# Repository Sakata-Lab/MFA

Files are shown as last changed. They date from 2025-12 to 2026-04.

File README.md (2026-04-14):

# Multi-fiber array (MFA)-based photometry system
This page provides resources for the publication on MFA development

## system
The folder contains an Excel file with a parts list to construct the optical system.

## grids
The folder contains three .stl files and a Python-based FreeCAD macro.

## fabrication
There is a PDF file detailing MFA fabrication procedures.

## MFA image processing workflow
The MATLAB LiveScript is the workflow for processing a .cxd file to analyse photometry signals.

## mfaCTpy: Python-based package for micro-CT image processing
https://github.com/Sakata-Lab/mfaCTpy 

This package allows:
- file conversion from .dicom files to a .tif file
- alignment to the midline
- registration to the Allen CCFv3
- manual tracing of individual fibers

## citation
If you find our work helpful, please use the following citations.
```
Multi-fiber array-based photometry system for multi-regional functional mapping in the mouse brain
Manil Bradai, Mirna Merkler, Gabriela Gil, Rebecca Davie, Shuzo Sakata
bioRxiv 2025.12.23.696162; doi: https://doi.org/10.64898/2025.12.23.696162

Multi-fiber array-based mesoscopic photometry  in the mouse brain
Manil Bradai, Mirna Merkler, Gabriela Gil, Rebecca Davie, Shuzo Sakata
https://github.com/Sakata-Lab/MFA
```

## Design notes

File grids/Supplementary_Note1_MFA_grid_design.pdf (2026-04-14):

## Supplementary Note 1

# Grid fabrication guide for multi-fiber array photometry system

Sakata Lab

## Introduction

For the multi-fiber array (MFA) photometry system (Bradai et al., bioRxiv 2025), 3D-printed grids are required to construct an MFA. The grid allows arranging multiple optical fibers to target multiple brain regions for various photometry experiments in vivo. In this document, we provide a manual to prepare grids with additional technical notes.

## Workflow

1. Designing a grid in FreeCAD
2. Exporting a CAD file as .stl file
3. 3D printing with Projection Micro Stereolithography (PµSL) technology

## 1. Designing a grind in FreeCAD

- Open FreeCAD

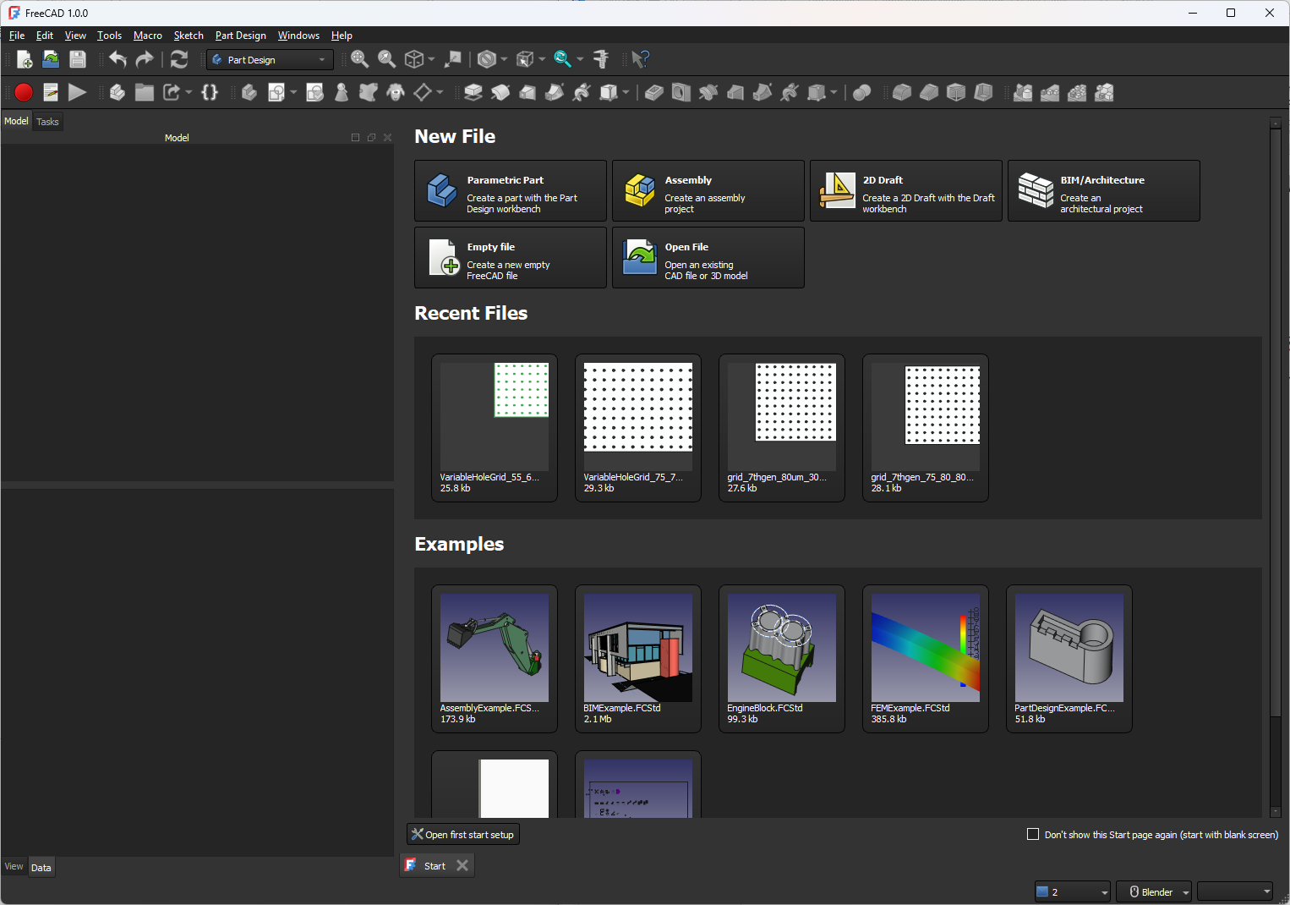
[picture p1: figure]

- File manu “Macro” > “Macros”

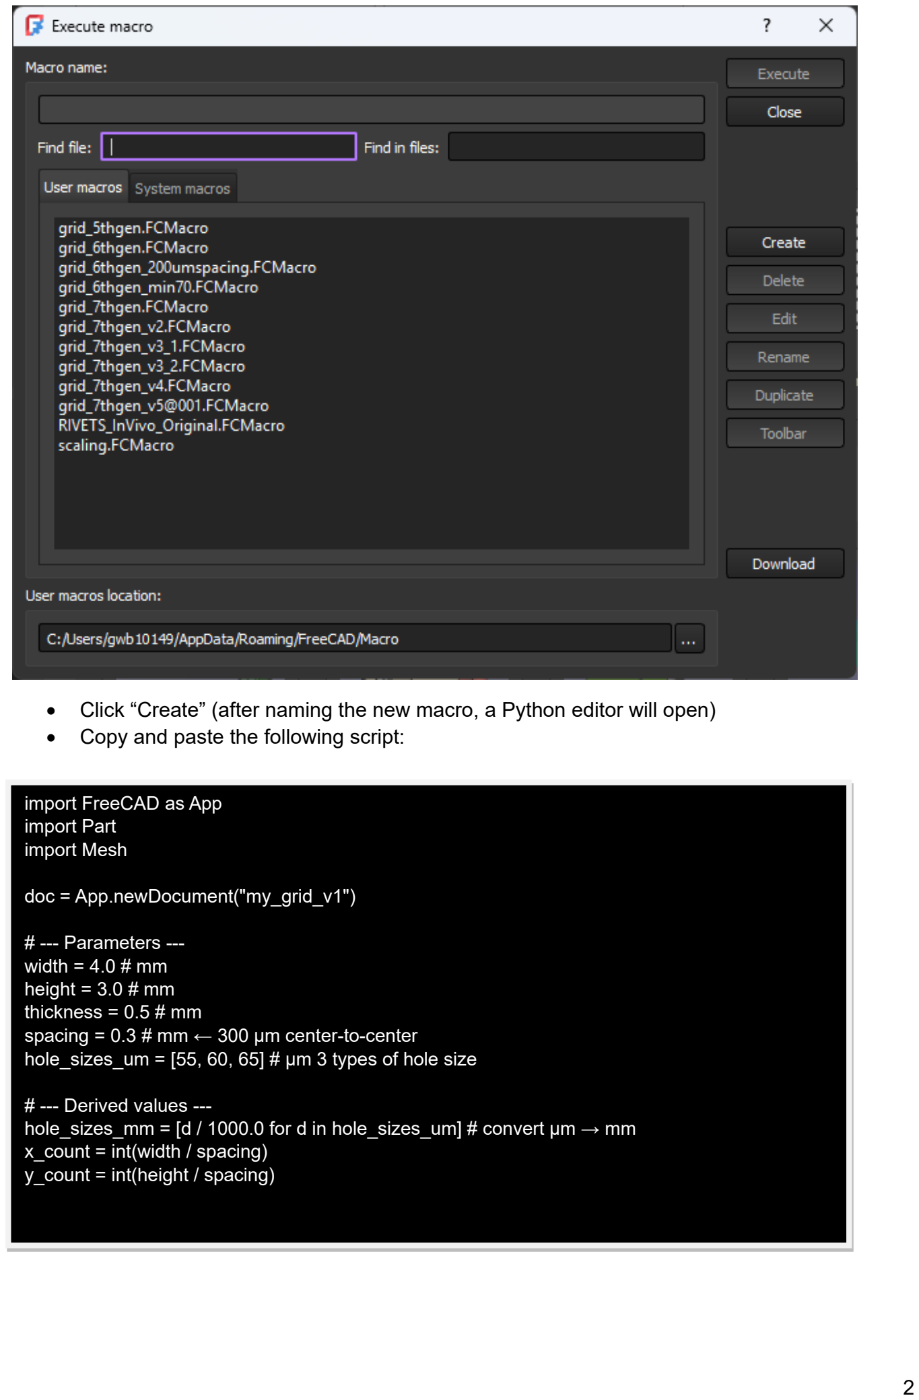
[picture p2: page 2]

- Click “Create” (after naming the new macro, a Python editor will open)
- Copy and paste the following script:

import FreeCAD as App
import Part
import Mesh

doc = App.newDocument("my_grid_v1")

# --- Parameters ---

width = 4.0 # mm
height = 3.0 # mm
thickness = 0.5 # mm
spacing = 0.3 # mm ← 300 µm center-to-center hole_sizes_um = [55, 60, 65] # µm 3 types of hole size

# --- Derived values ---

hole_sizes_mm = [d / 1000.0 for d in hole_sizes_um] # convert µm → mm x_count = int(width / spacing)
y_count = int(height / spacing)

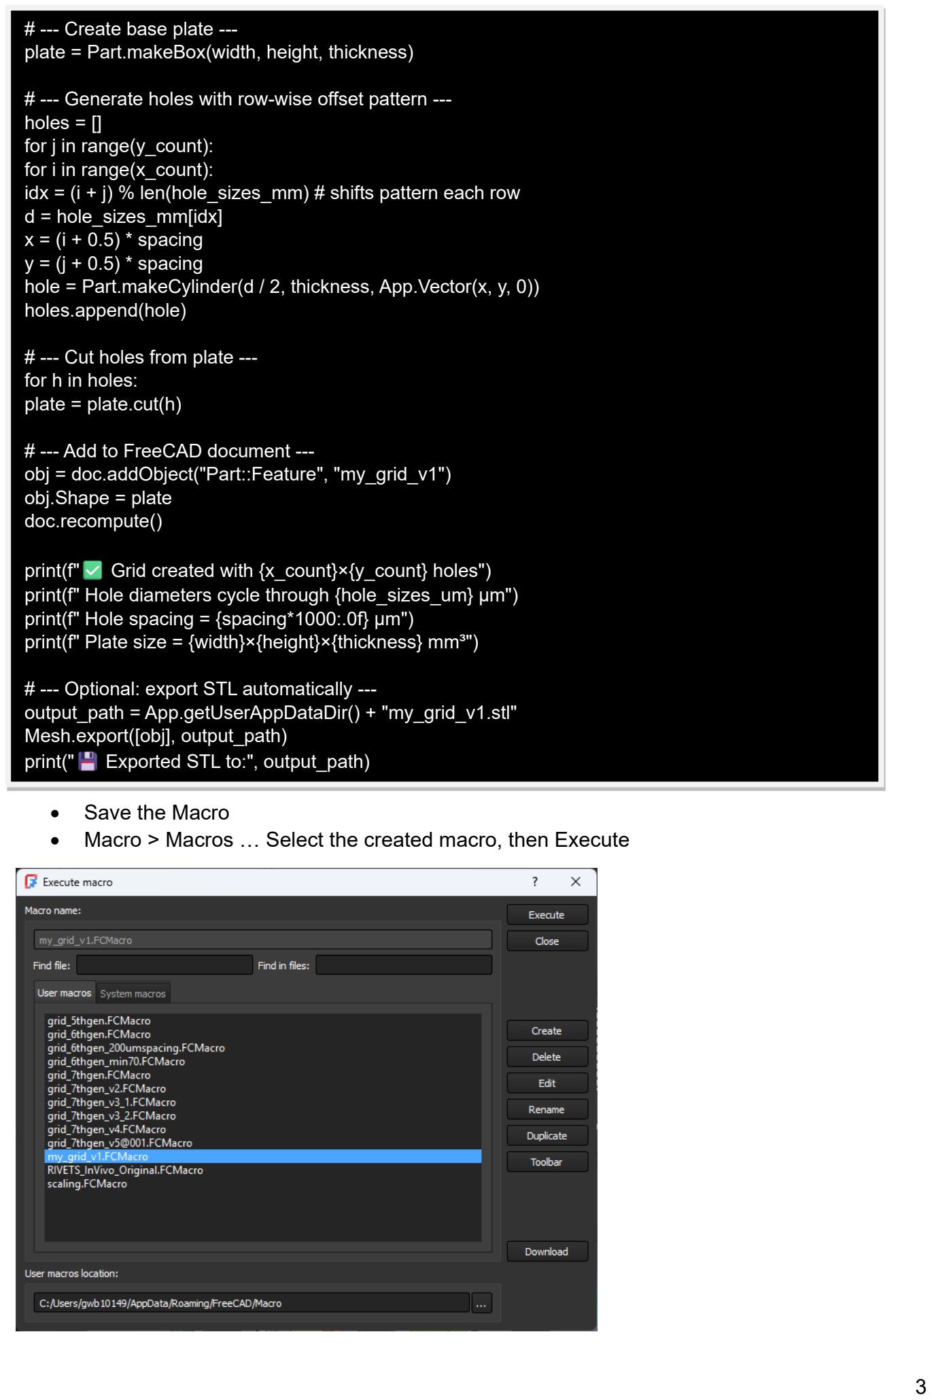
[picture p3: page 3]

- Save the Macro
- Macro > Macros … Select the created macro, then Execute

# --- Create base plate ---

plate = Part.makeBox(width, height, thickness)

# --- Generate holes with row-wise offset pattern ---holes = []

for j in range(y_count):
for i in range(x_count):
idx = (i + j) % len(hole_sizes_mm) # shifts pattern each row d = hole_sizes_mm[idx]
x = (i + 0.5) * spacing
y = (j + 0.5) * spacing
hole = Part.makeCylinder(d / 2, thickness, App.Vector(x, y, 0)) holes.append(hole)

# --- Cut holes from plate ---

for h in holes:
plate = plate.cut(h)

# --- Add to FreeCAD document ---

obj = doc.addObject("Part::Feature", "my_grid_v1") obj.Shape = plate
doc.recompute()

print(f" Grid created with {x_count}×{y_count} holes") print(f" Hole diameters cycle through {hole_sizes_um} µm") print(f" Hole spacing = {spacing*1000:.0f} µm")
print(f" Plate size = {width}×{height}×{thickness} mm³")

# --- Optional: export STL automatically ---

output_path = App.getUserAppDataDir() + "my_grid_v1.stl" Mesh.export([obj], output_path)
print(" Exported STL to:", output_path)

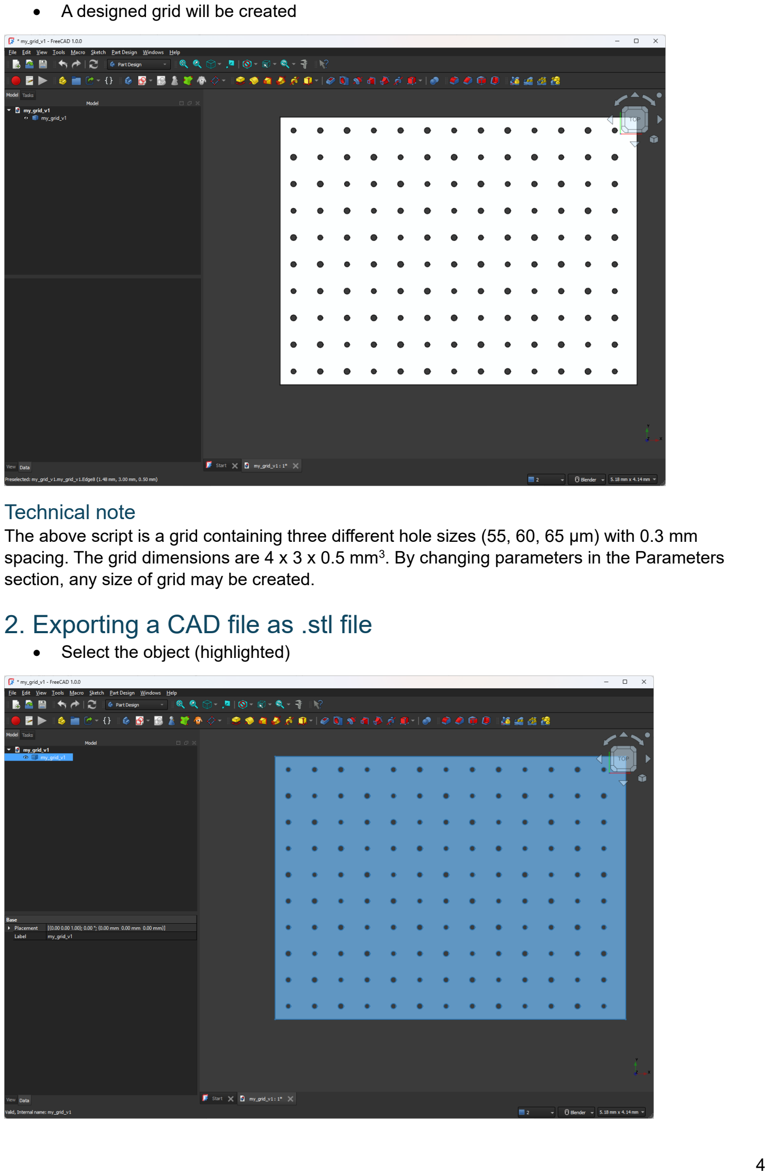
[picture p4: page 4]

- A designed grid will be created

Technical note
The above script is a grid containing three different hole sizes (55, 60, 65 µm) with 0.3 mm spacing. The grid dimensions are 4 x 3 x 0.5 mm³
. By changing parameters in the Parameters section, any size of grid may be created.

## 2. Exporting a CAD file as .stl file

- Select the object (highlighted)

- File > Export …
- Export as .stl file

## 3. 3D printing with PµSL technology

- Contact the company capable of Project Micro Stereolithography (PµSL) technology
- Sending the exported .stl file, grids can be printed

Company information
- BMF https://bmf3d.com/
- IPFL, https://www.ipfl.co.uk/

Any companies using PµSL, provided by Boston Micro Fabrication (BMF), should be able to print grids.

Technical note
At least two factors may be consulted with a company: (1) materials and (2) resolution
- Materials: High temperature liquid (HTL) is standard, but transparent. For opacity, carbon-based materials may be considered.
- Resolution: 2 µm or 10 µm resolution printing is available. The cost difference may be approximately 3x.

When grids are printed with carbon-based materials with 2 µm resolution, a 65~70 µm hole in the CAD file may be recommended since the actual hole size will become ~60 µm, which is suitable for 50 µm optic fibers.

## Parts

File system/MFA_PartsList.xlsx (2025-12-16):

product name | product number | qty | supplier
CMOS Camera
ORCA-Fusion BT | C15440-20UP | 1 | Hamamatsu Photonics
Main Body
Camera Port | WFA4100 | 1 | Thorlabs
Illumination Cube Housing | WFA2002 | 1
Microscopy Cube Assemly | MDFM-MF2 | 1
Dichroic Filter | MD498 | 1
Emission Filter | MF525-39 | 1
Cerna Body with Epi Arm | CEA1400 | 1
Aluminium Breadboard | MB4560/M | 1
Objective, Arm, Motorized Module
10x Fluorite Objective | RMS10X-PF | 1 | Olympus
Objective Arm | CSN100 | 1 | Thorlabs
Adaptor | M32RMSS | 1
Angle Bracket | PLSZ1 | 1
Motorized Module | PLSZ | 1
Stepper Controller | MCM301 | 1
USB Joystick | MCMK3 | 1
Light Sources
405 nm LED | M405L | 1 | Thorlabs
470 nm LED | M470L | 1
LED Holder | CP12 | 2
LED Driver | LEDD1B | 2
Aspheric Condenser Lens | ACL2520U-A | 2
Lens Tube | SM1L05 | 2
Cage Plate | CP08/M | 2
Filter Holder | C4W | 1
Kinematic Cage Cube Platform | B4C/M | 1
Dichroic Mirror | DMLP425R | 1
Peripheral (face camera)
Camera | aca1920-25um | 1 | Basler
Zoom Lens | M0814-MP2 | 1 | Computar
IR Filter | FGL780 | 1 | Thorlabs
IR LED Array | USB100W05MT-DL36 | 1 | ELP
Peripheral (DAQ)
DAQ Module | NI-USB-6002 | 1 | National Instruments
OR Gate | custom-made | 1 | RS components
Computer | Precision 5860 Tower | 1 | Dell

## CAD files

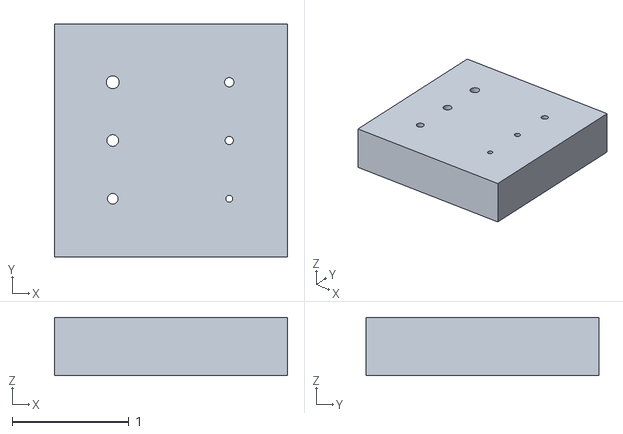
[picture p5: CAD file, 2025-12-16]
grids/grid_various_hole_sizes.stl
2.00 x 2.00 x 0.5

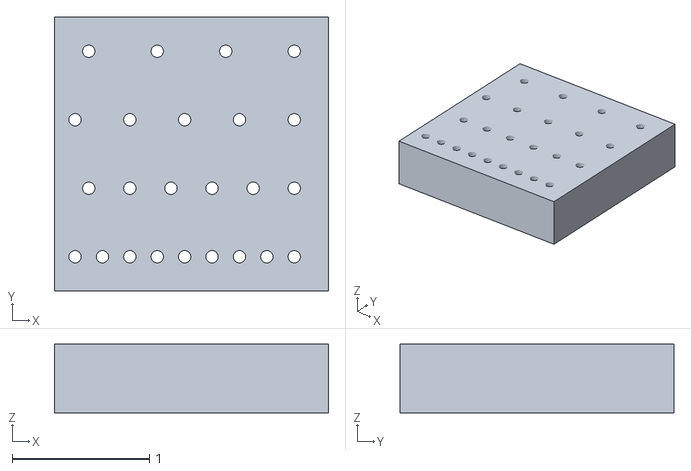
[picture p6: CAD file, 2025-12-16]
grids/grid_various_hole_distance.stl
2.00 x 2.00 x 0.5

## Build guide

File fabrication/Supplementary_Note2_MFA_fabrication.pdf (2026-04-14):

## Supplementary Note 2

# Multi-Fiber Array Construction Manual

## Gabriela Gil and Rebecca Davie

Table of Contents

## 1. Materials and Equipment

## 1.1 Consumables

Item | Manufacturer | Product Information
Optic fibers | Fiberoptics Technology Inc | Purewave XL66 1mmx30 Raw Fibre Bundle, 50µm, NA66
MFA grid | IPFL | Custom design
UV glue | Norland Products, Inc | Norland Optical Adhesive, NOA61, 1 OZ, 28.5g, LOT 612
Black Glue | RS Components | RS Pro, RT80 Black Cyanoacrylate, 20g, RS 908-2802
Pink Zap Glue | ZAP-A-GAP | ZAP CA Thin CA, 1 OZ (28.3g), PT-08
Solder Wire | MBO (UK) Ltd. | Solder Wire, 500g, 547-287
Acrylic Resin Liquid | Kemdent | Simplex Rapid Acrylic Liquid, 150ml, LOT 47557
Polishing Paper (green) | Thorlabs | 6x6 Inch, Diamond Lapping (Polishing) Sheets, 30µm Grit, LF30D
Polishing Paper (yellow) | Thorlabs | 6x6 Inch, Diamond Lapping (Polishing) Sheets, 6µm Grit, LF6D
Polishing Paper (pink) | Thorlabs | 6x6 Inch, Diamond Lapping (Polishing) Sheets, 3µm Grit, LF3D
Tubing | MicroLumen | Polyimide medical tubing, ID: 0.0710, OD:0.0988, Wall: 0.01390, 710-XV.5
Tubing | MicroLumen | Polyimide medical tubing, ID: 0.0477, OD:0.0578, Wall: 0.00505, 475-V.25
Reusable adhesive | Bostik | Blu Tack
Fluorescein HITC | Thermo Scientific Chemicals | Fluorescein Pure, 119240250

## 1.2 Tools and Instruments

Item | Manufacturer | Product Information
Optic fiber scribe | Thorlabs | FiberScribe, S90R
Stereoscope | Olympus | SZ51
Fiber Polishing Pad | Thorlabs | Silicone Polishing Pad, 50 duometer, 8.75x13 Inch (222.3mmx320.2mm) and 0.12Inch Thick (3.1m), NRS913A
Glass Polishing Plate | Thorlabs | Glass Polishing Plate, 9.5x13.5Inch and 0.5Inch Height, CTG913
LED Pen | Cakkone | CAT 2025 2 8
Digital Microscope | Ninyoon | 4K WIFI Microscope, 748521049947
Digital Microscope | Andonstar Technology Co.,Ltd. | AD106S
Tweezers | World Precision Instruments | Dumont Tweezers 5/45
Tweezers | TOWOT | Precision Tweezers, 5pcs Machine Tweezers Made of Stainless Steel Heat Resistant, SA13
Tweezers | Fine Science Tools | Graefe Iris Forceps, 11064-07
Scissors | World Precision Instruments | Operating Scissors 12/21, 501754-G
Optical system | See main text

## 2. Designing a Multi-Fiber Array (MFA)

This section outlines how to plan and design a customized MFA by identifying target brain regions, determining their anatomical coordinates using brain atlases, and arranging fibers on a spatial grid.

- Identify the target brain regions for optical recordings.
- Use the Paxinos and Franklin Mouse Brain Atlas to obtain stereotaxic coordinates for each region of interest.
- Define the MFA grid layout (e.g., 4 × 3 mm).
- Grid dimensions are fully customizable and should be adapted to the spatial distribution of the target regions.
- The spacing used here was 0.3 mm, resulting in linear offsets of 0.3 mm, 0.6 mm, 0.9 mm, etc.
- Note that spacing can be modified depending on experimental requirements.
- Map each fiber position on the grid to its corresponding anatomical target based on the stereotaxic coordinates.
- Adjust fiber lengths to ensure smooth implantation (e.g., adding an extra length to every fiber to improve visibility during implantation).

## 3. Preparation of Optical Fibers

This section covers how to set up a clean, organized workspace and prepare individual optical fibers for later assembly. It includes cutting, inspecting, and selecting viable fiber segments that will form the implantation array.

## 3.1 Workspace Preparation

- Lay out the Thorlabs silicone polishing pad on the Thorlabs glass polishing plate
- Spray the surface with antiseptic spray and wipe to clear any residue.
- Turn on the Andonstar digital microscope, prepare the Thorlabs fiber scribe, ruler and the Purewave fiber bundle.

## 3.2 Cutting and Organising Viable Fibers

- Pull out a fiber (be cautious of the glass) from the Purewave fiber bundle
- Place the fiber on the silicone polishing pad horizontally,
- With a ruler measure out approximate length of 3cm (anything longer can make the later stages harder) (Fig. 1A).
- Cut 3cm fiber segments by aligning the Thorlabs fiber scribe perpendicular to the fiber and gently slice in a one smooth motion
- Note that any excess pressure or pushing the blade directly into the fiber will result in damage.
- Inspect each of the cut fibers by holding them in tweezers no. 5/45 with a little bit of blu tack for better grip under the Andonstar digital microscope.
- Place suitable ends of the fibers facing one direction (these will be the ones used for implantation) (Fig. 1B)

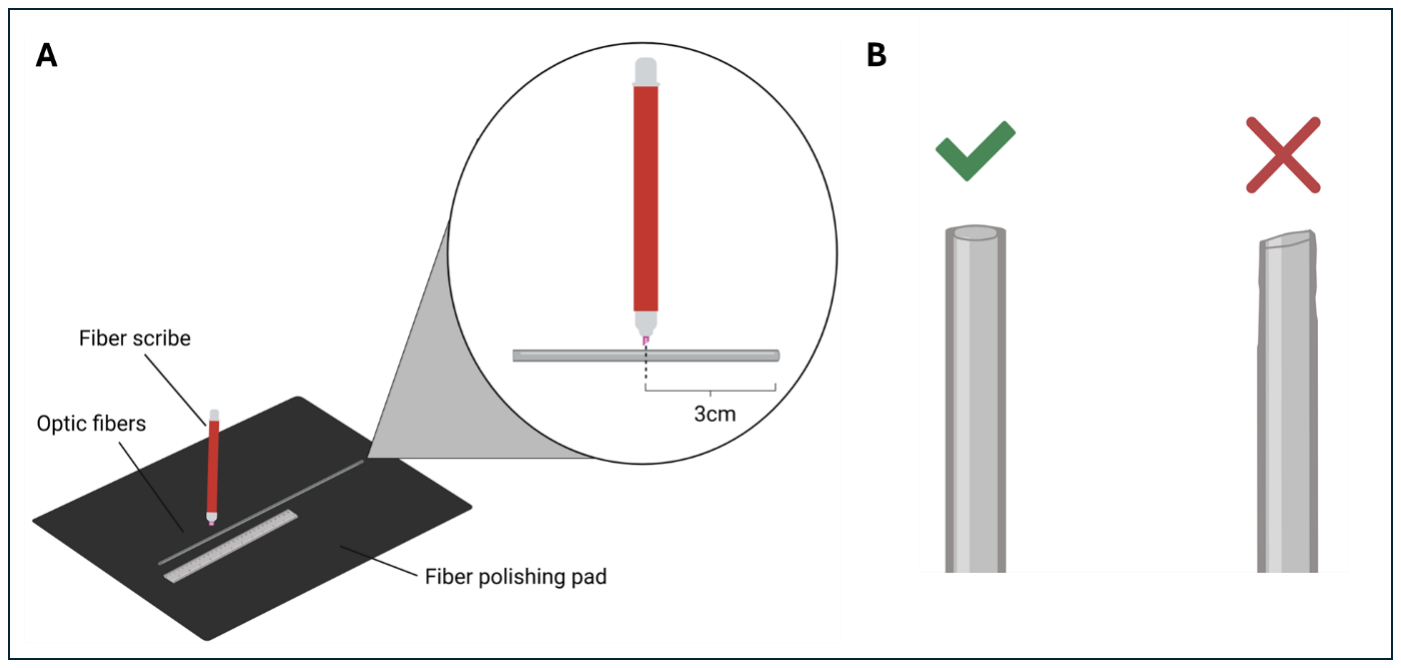
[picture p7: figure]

## 4. Preparing and Mounting the Grid

Explains how to position and stabilise the MFA grid so that its holes are clearly visible and accessible. Proper mounting is essential for successful fiber insertion in the next steps.

- Take the MFA grid (depending on the flexibility of the grid find the best way to mount it) and gently close inside of the tweezer no. SA13 securing vertically in the helping hand (Fig. 2)
- Note: Apply a thin layer of blue tack to inside to better grip
- Adjust the tilt of the grid under the Olympus Stereoscope, the holes of the grid should be all visible
- Check the stability of the set-up, this is crucial for the next step.
Figure 1 | Preparation and Cutting of Optic Fibers. Schematic illustrating the
procedure for cutting optic fibers. (A) A Thorlabs fiber scribe is positioned perpendicular to an optic fiber taken from the Purewave fiber bundle. The scribe is used to cut the fiber, producing a ~3cm segment. (B) Comparison of correct (left) and incorrect (right) fiber preparations following cutting. The left image shows a cleanly cut fiber with a smooth, flat imaging surface suitable for implantation. The right image shows a poorly cut fiber with a damaged, angled imaging surface that is unsuitable for implantation. Figures not to scale. Created in bioRender.

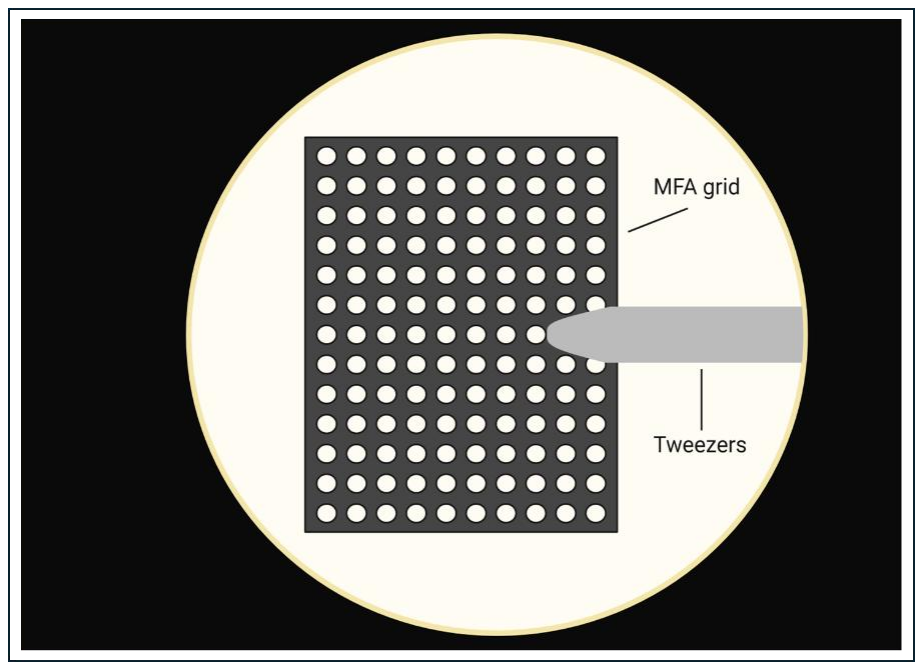
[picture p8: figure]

## 5. Loading Fibers into the Grid

This section describes how to measure implantation depth, mark fibers accordingly, and insert them into the grid in an organised, damage-minimising sequence. It concludes with securing all implanted fibers in place with adhesive.

## 5.1 Measuring Implantation Depth

- Using callipers measure out the length of the fiber implantation depth (Fig. 3)
- Note: refer to the MFA design ensure to factor in the thickness of the grid (0.5 mm) and offset (1 mm) for visualization of the brain surface during implantation.
- Use a soldering wire to place a drop Norland Optical Adhesive to mark the point of measured depth.
- Treat the adhesive drop with UWAVE curing pen for around 20 seconds (take any necessary precautions when using the UV light).
Figure 2 | MFA Grid Setup. Schematic representation of the stereoscopic view of the
MFA grid prior to fiber insertion. The grid is positioned between tweezers (no. SA13) lined with a thin layer of blu tack. The tweezers are held in place using helping hands. Figure not to scale. Created in bioRender.

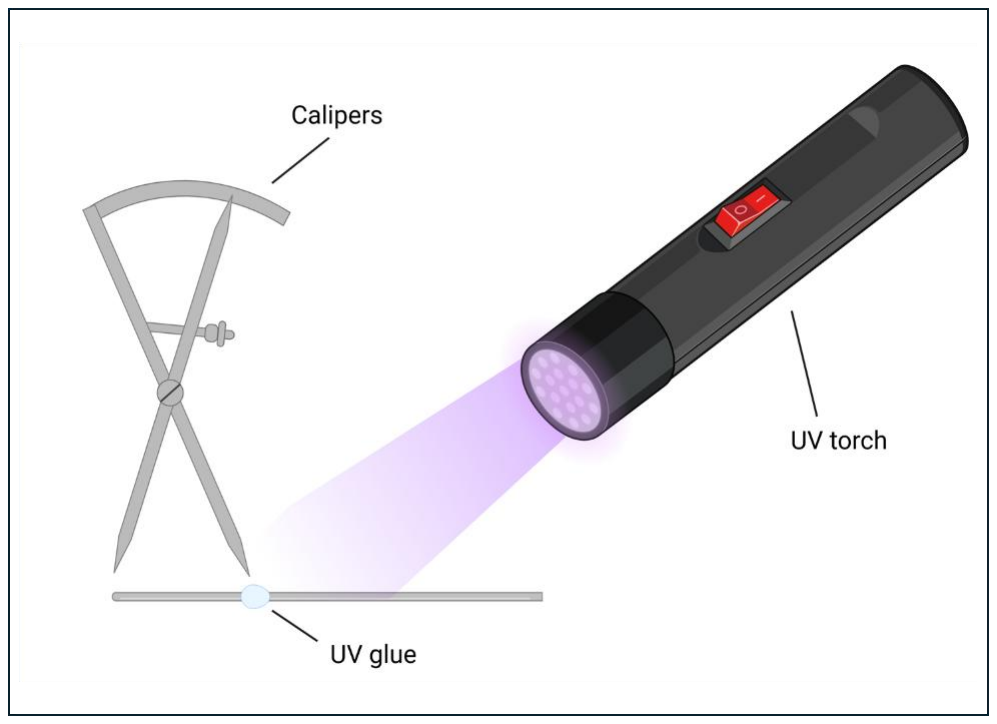
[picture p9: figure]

## 5.2 Insertion Procedure and Securing Fibers in Grid

- In reference to the MFA design, start from the top of the grid and work your way across the rows (this will help avoid the distal ends of the fibers breaking) (Fig. 4A).
- To insert the cured fibers, use blue tack lined tweezers no. 5/45 and hold approximately 1/3 from the implantation end to insert cured fibers into assigned grid hole
- Note: avoid tapping the end on the grid as this may result in the site being fractured = low efficiency.
- Once all the fibers have been inserted (Fig. 4B), carefully tilt the grid so that it lies perfectly parallel to the workbench.
- Using the soldering wire, place drops of UV glue (NOA61, Norland Products) on the top of the grid. The droplet should spread across the grid, then secure the fibers in place with a UV light.
Figure 3 | Measurement and Marking of Fiber Implantation Depth. Schematic
illustrating the procedure for measuring and marking fiber implantation depths prior to insertion into the MFA grid. Calipers are used to measure the length of the fiber segment to be implanted in reference to the MFA design. The thickness of the grid is included in the final caliper measurement. The measured depth point is marked with UV glue and cured using an UV torch. Figure not to scale. Created in bioRender.

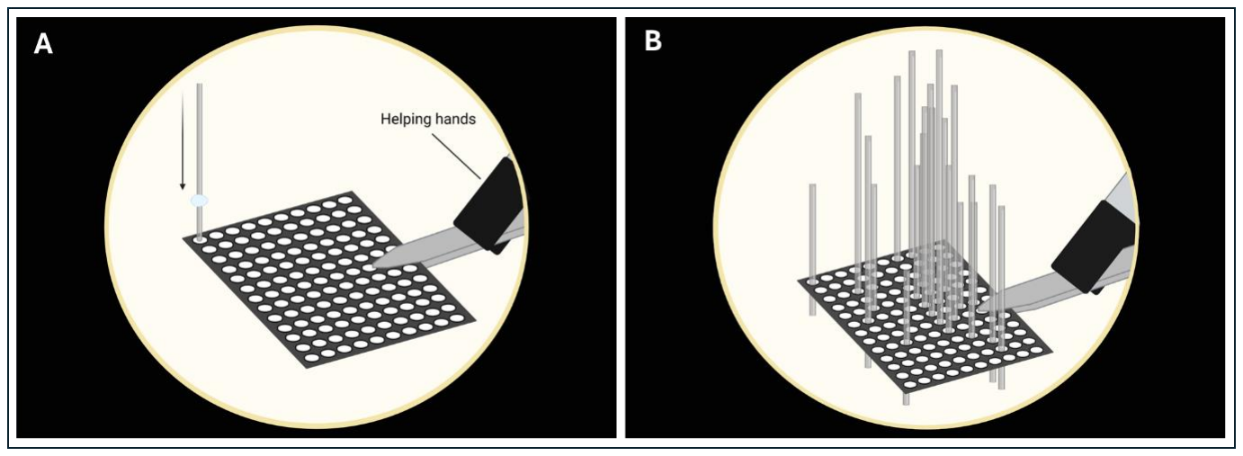
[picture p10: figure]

## 6. Securing and Encasing Distal Fiber Ends

This section describes how to gather, insert, and fix the distal (non-implanting) ends of the fibers inside a protective tube, creating a stable bundle for imaging.

## 6.1 Tubing Placement

- Cut an 8mm piece using a scalpel Microlumen tubing.
- Note: Depending on the number of fibers being implanted choose a suitable size of the Microlumen tubing
- Bundle the distal (non-implanting) ends of the fibers by gently gathering them with moistened fingertips (Fig. 5A)
- Navigate the bundle into the cut Microlumen tubing (Fig. 5B).
Figure 4 | Loading Fibers into the MFA Grid. Schematic representation of the
stereomicroscopic view of the fiber loading process. (A) According to the MFA design, cured fibers are inserted into the MFA grid. Beginning at the top of the grid, fibers are inserted row by row (top to bottom) and column by column (left to right). (B) Shows a fully loaded MFA grid. Figures not to scale. Created in bioRender.

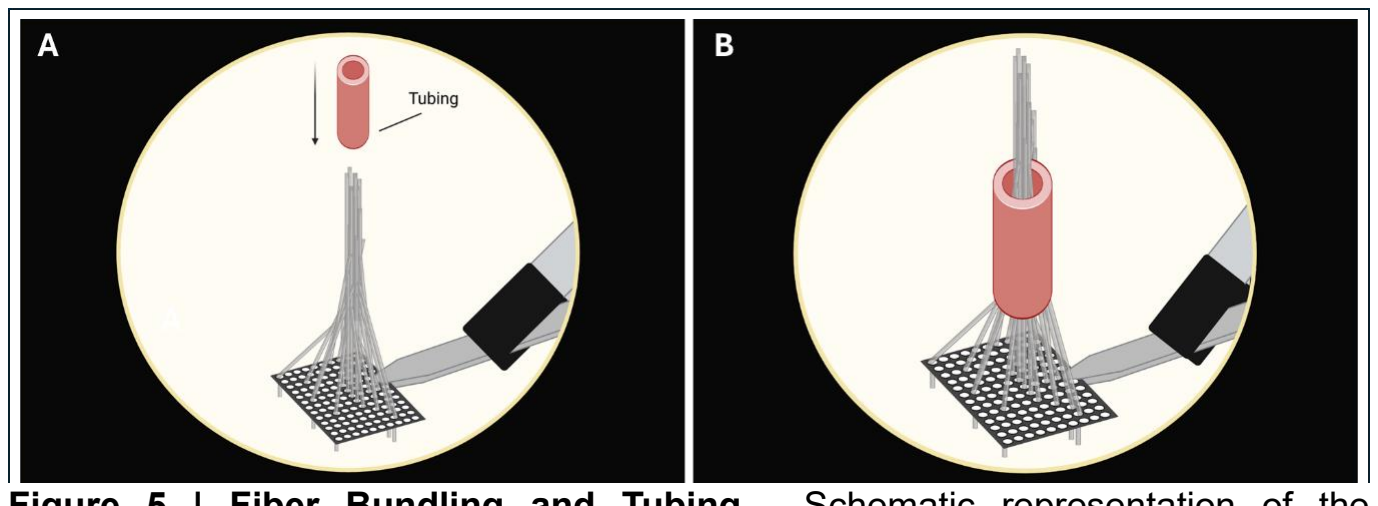
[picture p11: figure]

Figure 5 | Fiber Bundling and Tubing. Schematic representation of the
stereomicroscopic view of fiber bundling and tubing placement process. (A) The distal fiber ends are bundled together using moistened fingertips. (B) Microlumen tubing is then lowered to collect the bundled distal ends. Figures not to scale. Created in bioRender.

## 6.2 Filling Tube with Adhesive

- Using a micro syringe pull ZAP Thin CA glue, avoiding air bubbles (Fig. 6).
- Face the needle towards you, and controlling the decant flow of the glue into the tube fill approximately ¼
- Allow the first layer of glue to dry out (around 10min)
- Once the first layer is dry continue to fill the tube in the same manner, make sure the tube is filled to the brim but not overflowing.
- Leave to dry overnight.
- Note: It is key to avoid air bubbles as this will impact the imaging surface

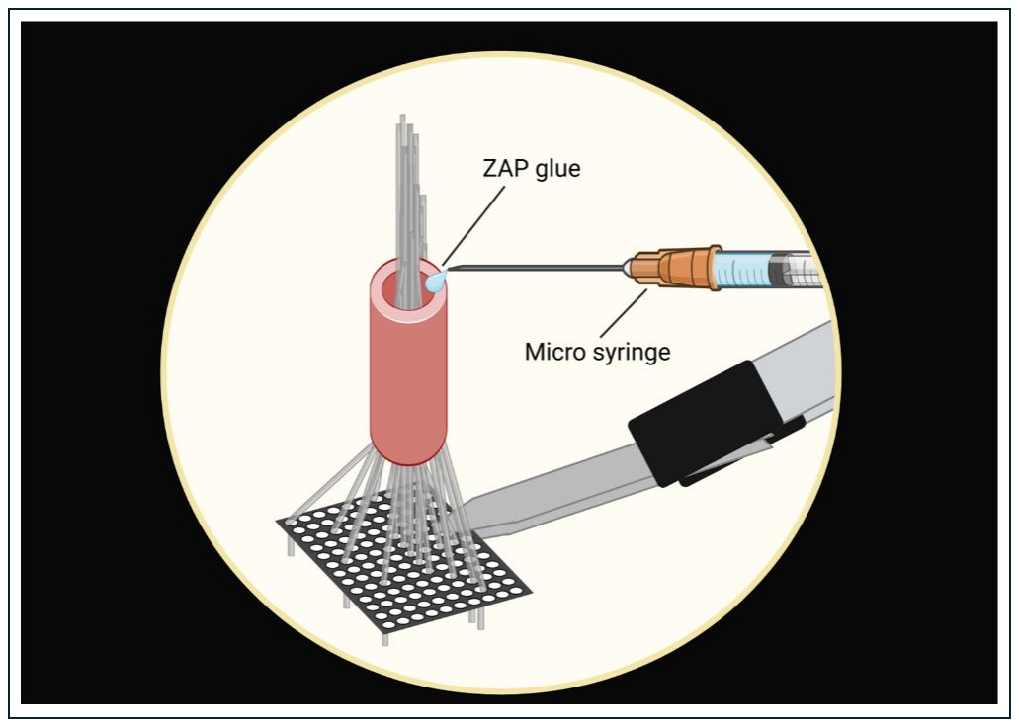
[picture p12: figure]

## 7. Encasing MFA and Polishing the Imaging Surface

This section details how to reinforce the MFA with additional adhesive layers and polish the distal surface to ensure a smooth, optically clean imaging area.

## 7.1 Encasing the grid

- Cut off a short piece of the soldering wire and create a circle
- Slide the Microlumen tube of the MFA halfway into it and tighten the wire, you may wrap the wire around again to ensure stability and twist the ends to secure (Fig. 7A).
Figure 6 | Filling Tubing with Adhesive. Schematic illustrating the process of filling
the microlumen tubing with ZAP glue. A micro syringe is used to draw ZAP glue, which is slowly dispensed into the tubing, allowing approximately 10 minutes between layers. This process is repeated until the tube is filled. Figure not to scale. Created in bioRender.

- Insert the twisted part of the wire into the helping hand and adjust the MFA so that it is parallel to the workbench.
- Use soldering wire to place drops of the RT80 Black Cyanoacrylate to create layers starting from the grid towards the top of the tube. Allow the glue to spread between the fibers (Fig. 7B).
- Allow layers to dry out before proceeding with the next one
- Optional: you can use a drop of Rapid Acrylic liquid to speed the drying process).
- Make sure to cover the red tubing with the black glue to protect the fibers from light and allow to dry

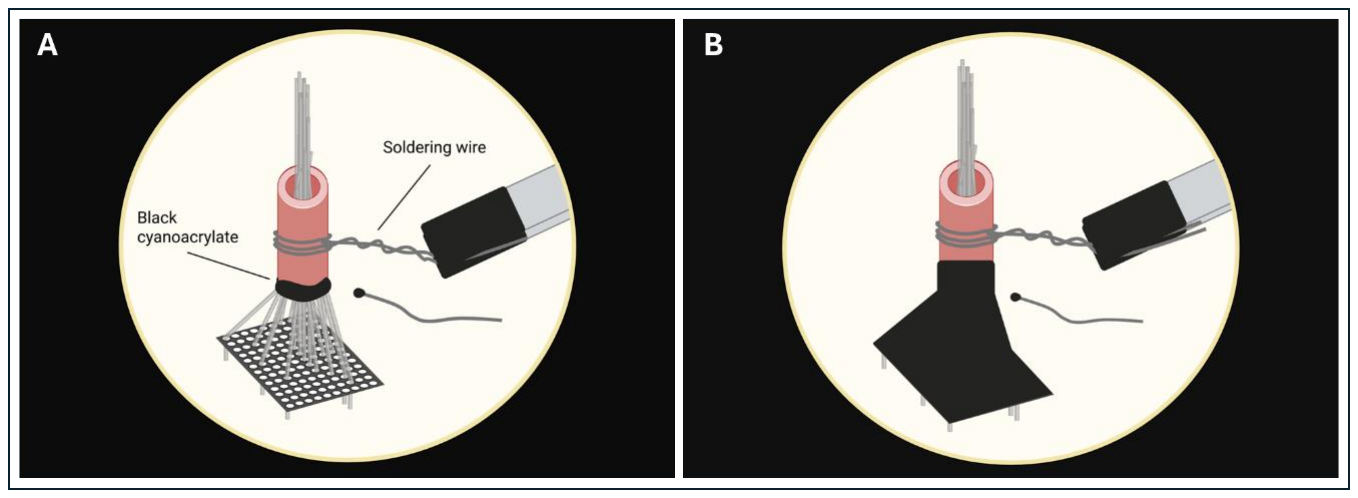
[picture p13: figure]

## 7.2 Rough Cutting and Polishing Sequence

- Use scissors to trim the distal fiber bundle (you may consider cutting part of the tubing along with it) (Fig. 8A).
- Lay out three Thorlabs Diamond Lapping (polishing) sheets of different grit 30µm (green), 6µm (yellow), 3µm (pink).
- Add a drop of distilled water to each of the papers and spread with your finger.
- Grip the tube with tweezers no. 11064-07 and holding the tweezers perpendicular to the paper throughout, using circular motion, polish the surface of the tube for 2 minutes on each of the papers starting with the highest grit (Fig. 8B).
- Using the stereoscope examine the imaging surface, ensure the surface is flat and no major air bubbles are obstructing the imaging area.
- Note: If the surface still looks uneven you may repolish the tube using the 3µm grit.
Figure 7 | Encasing the MFA. Schematic representation of the stereomicroscopic
view of encasing the MFA with black cyanoacrylate. (A) The MFA is repositioned in the helping hands using soldering wire. A segment of soldering wire is dipped in black cyanoacrylate and is used to apply adhesive around the base of the microlumen tubing. (B) A fully encased MFA is shown. Repeat this process, covering the bottom of the microlumen tubing, exposed fibres, and grid is repeated until the MFA is fully encased. Figures not to scale. Created in bioRender.

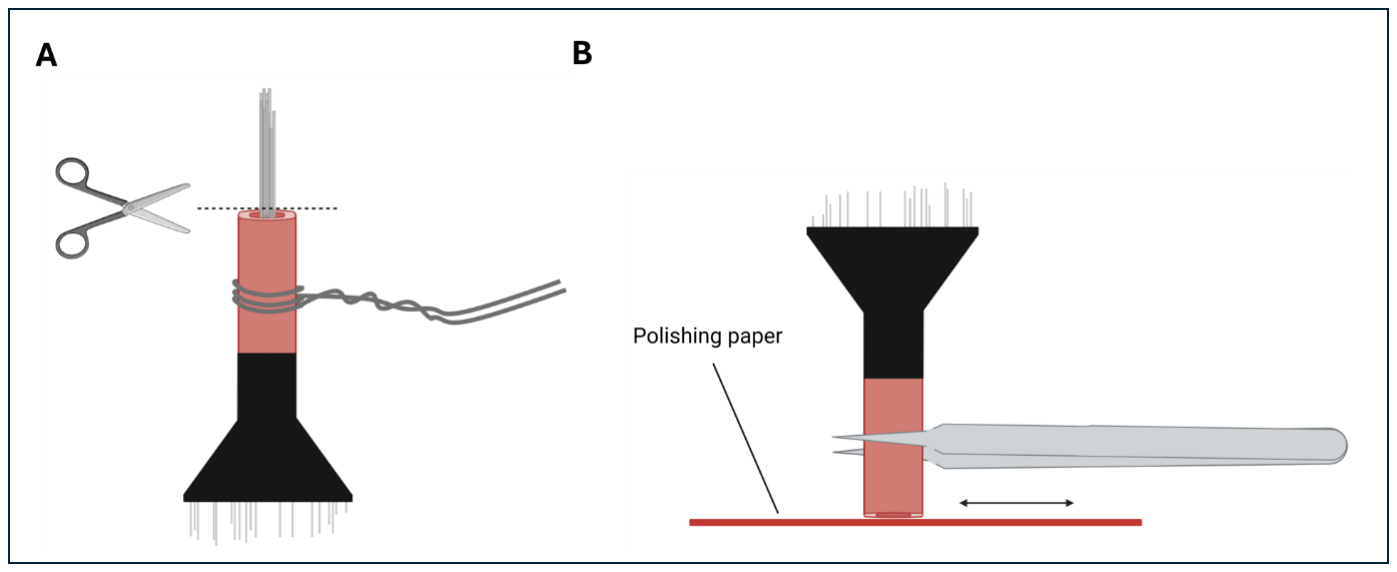
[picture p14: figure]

## 8. Fiber Mapping

This section describes how to identify the correspondence between each implanted fiber’s grid position and its position on the polished imaging surface. This map is essential for later data interpretation.

## 8.1 Setup

- Rotate the MFA so that the implantation site is facing upwards and secure in the helping hands by clamping the twisted soldering wire (Fig. 9).
- Position the Olympus stereoscope so that you can clearly see the implantation fibers and which row/columns they sit in.
- Turn on the digital Ninyoon WIFI Microscope and place it below the MFA. On your cellular device download the WiFi application (e.g. phone, tablet) you should see the bundled fibers inside the tube (imaging surface).
Figure 8 | Polishing the Imaging Surface. Schematic of the removal of distal ends
and subsequent polishing of the MFA imaging surface. (A) Scissors are used to trim distal fiber ends. (B) The MFA is removed from the soldering wire grip and held with tweezers (no. 11064-07). Holding the MFA perpendicular to the polishing paper, the surface is polished using a back-and-forth or circular motion. This process is repeated for each polishing paper. Figures not to scale. Created in bioRender.

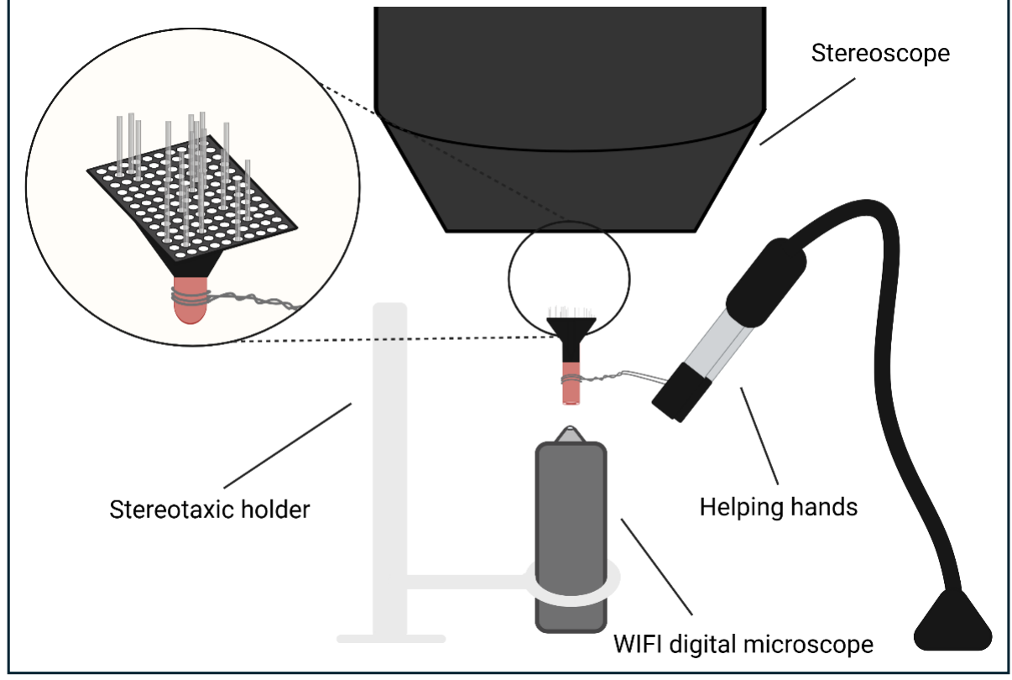
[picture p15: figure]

## 8.2 Mapping Procedure

- Using a small, 90° folded piece of paper (preferably black) isolate the fibers in the grid row by row going from bottom to top (Fig. 10A).
- Shine an LED light pen on the isolated fiber, the fiber should light up on the screen of your cellular device – make a note of which grid coordinate (refer to MFA design) the fiber corresponds to on the imaging surface (keep in mind the image displayed is inverted) (Figs. 10B&C).
- Note: For rows with multiple fibers, take an additional piece of card to individually isolate the fibers of interest by blocking them from the LED light and following the same process of discrimination.
Figure 9 | MFA Mapping Setup. Schematic of the preparation and set up for the
mapping procedure. The MFA is rotated so that the implantation site is facing upwards towards the stereoscope and is secured using soldering wire and helping hands. A WIFI camera is positioned beneath the imaging surface and is held in place with a stereotaxic holder. The circular inset at the top left shows the stereoscopic view of the setup. Figure not to scale. Created in bioRender.

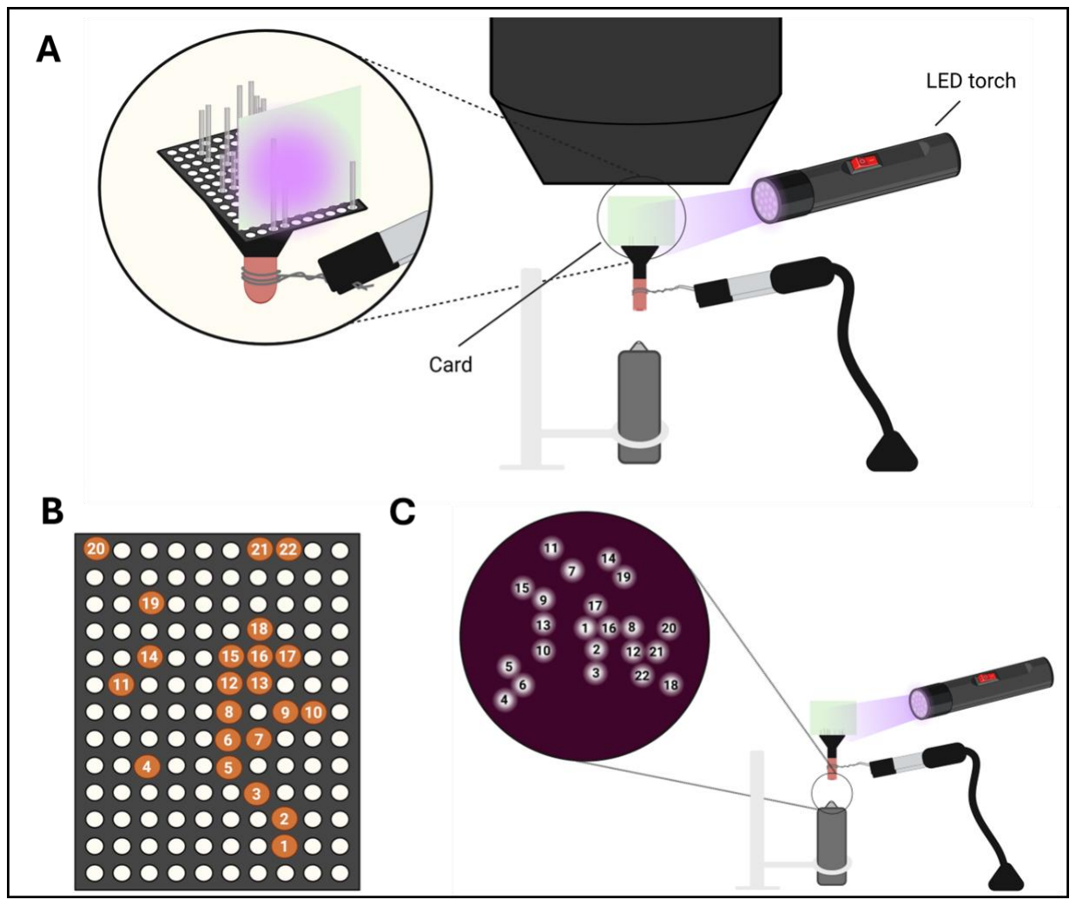
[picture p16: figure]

## 9. Quality Control (QC) and Functional Validation

This section outlines how to validate the functional performance of the MFA using fluorescence testing and image analysis, ensuring the array transmits signals reliably.

## 9.1 Fluorescence Transmission Testing

- Prepare Fluorescein (TH+) solutions at different concentrations by diluting in PBS; 0µM (PBS), 0.1µM, 0.5µM (optional) and 1µM.
- Place the solutions in the eppendorfs and secure in the eppendorf rack.
- Mount the MFA on the stereotaxic manipulator and lower the implantation ends into the solution starting with the lowest concentration 0µM (PBS).
Figure 10 | MFA Mapping Setup. Schematic illustrations of the mapping procedure.
(A) Setup of the mapping process. Beginning with the bottom row containing a fibers, a piece of card is inserted behind each fiber to isolate it. This is repeated row by row (bottom to top) and column by column (left to right). An LED torch is directed at the isolated fiber, producing illumination visible on the mobile device connected to the WIFI camera. (B) The MFA design, showing the numbering of each fibre according to its layout (bottom to top, left to right. Using this design, the illuminated fiber can be identified on the mobile device screen. (C) Digital microscope setup and inset showing mobile device view of MFA imaging surface with illuminated fibers. The visible fibers are numbered according to the MFA design. Figures not to scale. Created in bioRender.

- Using sCMOS camera connected to the HCImage software observe the imaging surface and capture fluorescence at 405nm (isosbestic) and then at 470nm excitation wavelengths, both on 5V.
- Note: Ensure not to change the parameters between capturing, repeat this for each of the concentrations.

## 9.2 Data Capture and Analysis

- The captured images should be processed in the MATLAB.
- The analysis should result in a calibration curve, if QC is successful the calibration curve should be linear.
- Note: If you have any issues, you may consider repolishing the imaging surface on the lowest 3µm grit again.
